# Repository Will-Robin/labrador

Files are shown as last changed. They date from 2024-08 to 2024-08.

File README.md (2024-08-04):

# labrador

Code and designs for a drop-counting assembly.

# Usage

Make sure the hardware and software construction/installation instructions have
been completed before going further.

Note that upon execution of the script, a folder called `data` will be created
in the same directory as the program. This folder stores data collected by the
program (drop times).

## Running labrador

Double click the executable and follow the instructions in the terminal which
pops up. Note that the program may receive commands from your keyboard, even if
the window is not focussed.

## Developer mode: running labrador in a Python environment

Execute `python src/labrador.py` and follow the instructions in the
terminal.

# Installation/ Building

## Hardware

The `designs` directory contains the design for a bracket which will fit onto a
Biorad fraction collector and house the drop sensor. If you wish to edit the
design, the source Blender file is supplied, as well as the .stl file.

Load the .stl file into the slicing software supplied with your 3D printer. The
exact details of the slicing procedure will depend on the printer and material
you wish to use. A successful print was made using a Flashforge Guider IIs using
the settings in `designs/printer.fcfg`.

Once the bracket has been printer, de-solder the LED and infra-red sensor from a
KY-032 infra-red obstacle avoidance module. Re-make the connections using
flexible wiring such that the LED and IR receiver can reach and fit into the
round and rectangular holes of the bracket, respectively, whilst the body of the
sensor is placed on the peg in the housing on the side of the bracket with the
connection pins facing up. Place the LED and IR receiver into their respective
holes on the bracket. They may need to be held in place with some hot glue.

Next, connect the Arduino to your computer, and open `Arduino/labrador` in the
[Arduino IDE](https://docs.arduino.cc/software/ide-v2). Instructions on how to
load programs such as `labrador.ino` onto the Arduino should be easily found
online.

Use `list_com_ports.py` to find the `pid` and `vid` of the device. Copy these
values into `src/labrador.py` (the `pid` and `vid` variables).

Attach the ground and power pins of the IR sensor to the ground and 5V
connections of the Arduino, respectively. Connect the output pin of the IR
sensor to pin 2 of the Arduino. Connect the Arduino to a USB port on your
computer. You should be able to test if every is connected OK using your finger
to block the IR beam. The `Sled` light on the IR sensor should be lit, but will
extinguish when the beam is blocked. Simultaneously, The 'RX' LED on the Arduino
board will temporarily turn off, whilst the 'L' LED turns on.

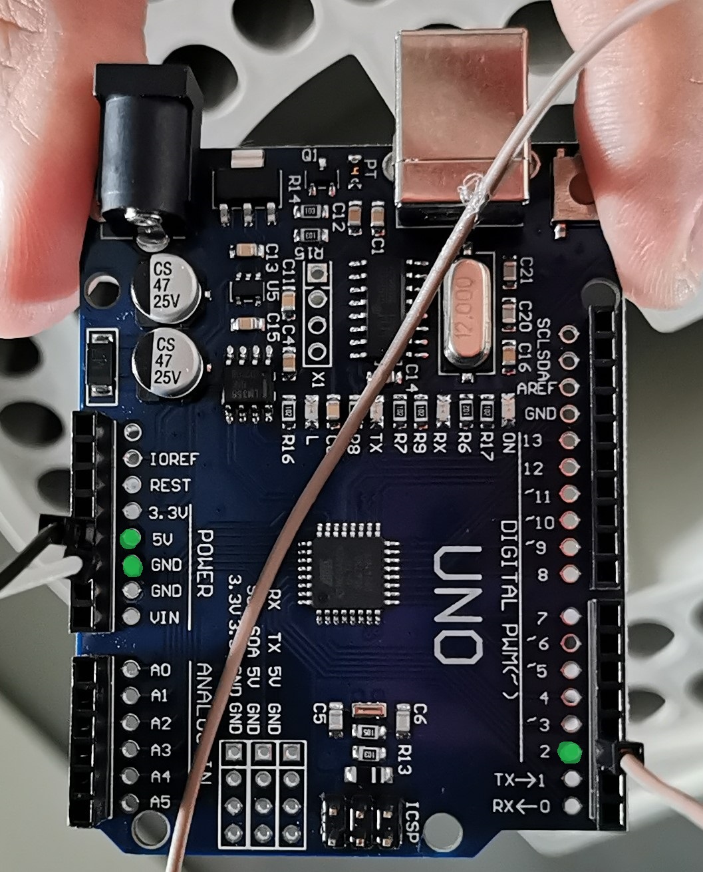
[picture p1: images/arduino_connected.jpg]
Connections made to the Arduino


Now the hardware is ready, go to the software step.

## Software Installation

These software can be run in a Python environment with all required dependencies
installed (see `setup.py`). For portability, the software can also be compiled
into an executable using `pyinstaller`. This can be performed simply if you have
`Make` installed (execute `make` in the terminal). If you do not want to use
`Make`, make sure all of the dependencies are installed (including the extras in
`setup.py`), and run:

```
pyinstaller src/labrador.py --onefile
```

The resulting executable is saved in `dist/`, and can be moved to another
location for execution.

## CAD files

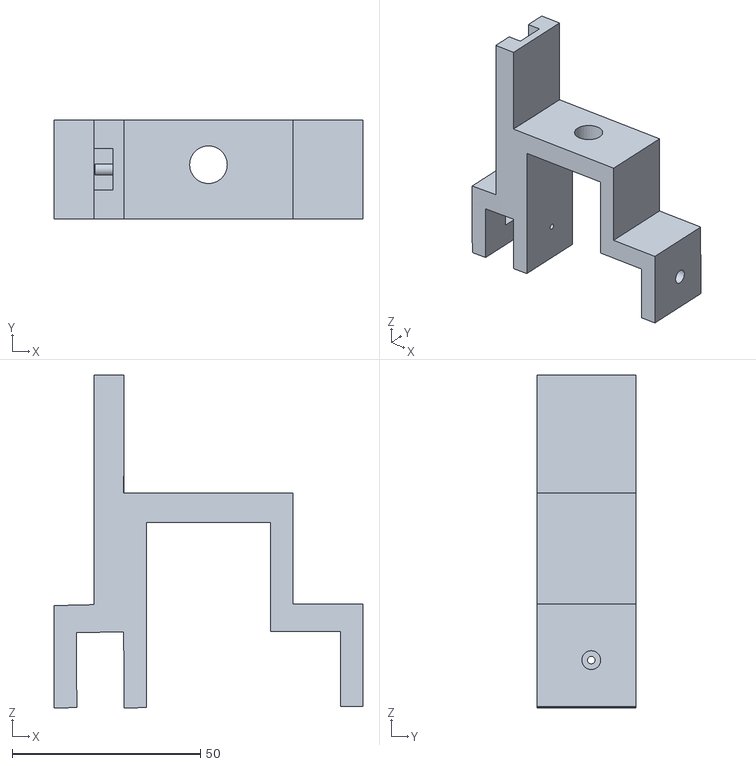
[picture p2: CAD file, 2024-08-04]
designs/Biorad_drop_sensor.stl
82.0 x 26.4 x 88.4

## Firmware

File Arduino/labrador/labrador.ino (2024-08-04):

int LED = 13; // LED to flash when drop is detected
int isObstaclePin = 2;  // input pin
int isObstacle = HIGH;  // HIGH mean no drop
int waitTime = 1000; // Minimum time to wait between drops
int baudRate = 9600;

void setup() {
  pinMode(LED, OUTPUT);
  pinMode(isObstaclePin, INPUT);
  Serial.begin(baudRate);
  digitalWrite(LED, LOW);
}

void loop() {
  isObstacle = digitalRead(isObstaclePin);
  if (isObstacle == HIGH) // drop detected
  {
    Serial.println(1);
    digitalWrite(LED, HIGH);
    delay(waitTime); // Wait before next trigger
  } else if (isObstacle == LOW) {
    Serial.println(0);
    digitalWrite(LED, LOW);
  }
}
